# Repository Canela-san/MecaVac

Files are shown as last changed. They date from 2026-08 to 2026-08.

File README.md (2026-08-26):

# MecaVac

*Refrigerador inteligente para vacinas — controle de temperatura, monitoramento de porta e log de eventos em ESP32.*

**Mecatron Projetos e Consultoria Jr.** · Hardware (Altium Designer) + Firmware (ESP32 / PlatformIO) · 2022 · Projeto concluído e aprovado pelo cliente; descontinuado após a primeira versão.

Este repositório reúne o firmware, o projeto de hardware e a documentação técnica do MecaVac — internamente registrado na Mecatron como *Refrigerador de Vacinas* (projeto nº 0000034). Ele também guarda o histórico real de desenvolvimento: sketches de bancada, versões intermediárias do firmware e o início (incompleto) de uma segunda revisão, mantidos aqui como registro de como o projeto evoluiu, não como parte do build final.

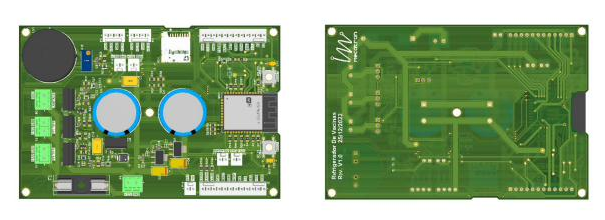
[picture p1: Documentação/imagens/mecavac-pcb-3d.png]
Renderização 3D da PCB do MecaVac — topo e fundo

gora
## Sumário

- [Sobre o projeto](#sobre-o-projeto)
- [Minha atuação](#minha-atuação)
- [Como funciona](#como-funciona)
- [Funcionalidades](#funcionalidades)
- [Hardware](#hardware)
- [Firmware](#firmware)
- [Estrutura do repositório](#estrutura-do-repositório)
- [Compilando e gravando o firmware](#compilando-e-gravando-o-firmware)
- [Lições aprendidas e limitações conhecidas](#lições-aprendidas-e-limitações-conhecidas)
- [Tecnologias utilizadas](#tecnologias-utilizadas)
- [Status do projeto](#status-do-projeto)
- [Licença e uso](#licença-e-uso)
- [Autor](#autor)

## Sobre o projeto

O MecaVac é um refrigerador para armazenamento de vacinas, desenvolvido sob demanda de um cliente que precisava de um equipamento com controle de temperatura confiável e rastreabilidade do que acontece dentro dele: quando a porta é aberta, quando uma vacina é retirada, e o que acontece em caso de queda de energia.

O equipamento final integra:

- placa de circuito impresso customizada, com ESP32 como controlador central;
- acionamento de dois módulos Peltier (TEC) para refrigeração, controlados por PWM;
- sensoriamento de porta, temperatura, retirada de vacina e falha dos módulos Peltier;
- display LCD local para status e configuração de data/hora;
- log de eventos em cartão microSD, com backup de energia via supercapacitores;
- provisionamento de Wi-Fi via portal cativo, para envio de status e logs a um servidor do cliente.

O projeto passou por testes de bancada e de campo, foi validado e aprovado pelo cliente. Depois da entrega, ficou claro que a primeira versão tinha vários pontos a melhorar (ver [Lições aprendidas](#lições-aprendidas-e-limitações-conhecidas)) — mas o custo de uma segunda revisão de hardware não se pagou para o cliente, e o projeto foi encerrado nessa primeira versão.

## Minha atuação

Entrei na Mecatron Jr. ainda no primeiro ano da faculdade, como Assessor de Projetos, e o MecaVac acabou ficando comigo do início ao fim: concepção, hardware, firmware, documentação e as reuniões — tanto internas quanto com o cliente que pagou pelo desenvolvimento. Como em qualquer empresa júnior brasileira, a atuação foi voluntária (empresas juniores não podem remunerar seus membros), mas foi a experiência mais próxima de um projeto real que tive até então: cliente pagante, prazo e responsabilidade técnica de ponta a ponta.

Principais responsabilidades:

- projeto completo da PCB no Altium Designer — esquemático, seleção de componentes, roteamento e liberação para fabricação;
- desenvolvimento do firmware em C/C++ (ESP32, PlatformIO);
- definição da arquitetura de log local (SD) e de comunicação com o servidor do cliente;
- documentação técnica do hardware e do firmware;
- interlocução direta com o cliente e com a diretoria da empresa júnior.

Aprovação técnica do projeto (Mecatron Jr.): Nisio José S. Neto.

## Como funciona

Em operação normal, o ESP32 lê periodicamente os três sensores de temperatura (DS18B20, barramento OneWire) e calcula a média entre as duas sondas do compartimento de vacinas. Essa média é comparada a uma temperatura ideal (6 °C) e o firmware ajusta a potência aplicada aos dois módulos Peltier em quatro patamares (0%, ~27%, ~50% e 100% de duty cycle), de acordo com o quanto a leitura está fora da faixa aceitável.

Um sensor magnético detecta a abertura da porta: ao abrir, a luz interna acende e o LED de status muda de verde para vermelho; se a porta ficar aberta além de um tempo configurável (10 segundos na versão final), o buzzer soa até que a porta seja fechada ou um dos botões externos seja pressionado. Cada módulo Peltier tem um sensor próprio de funcionamento, permitindo detectar falha em um dos dois de forma independente.

Um relógio de tempo real (DS1307) mantém data e hora mesmo sem conexão, usadas tanto na exibição do display quanto na marcação dos eventos gravados no cartão microSD. Se a alimentação principal cai, um sensor de queda de energia dispara e o firmware grava esse evento no SD — o equipamento continua ligado por alguns segundos graças a dois supercapacitores de 1F carregados por um circuito de soft-start, tempo suficiente para o log ser gravado com segurança antes do desligamento total.

Na primeira inicialização (ou após um reset de configurações), o dispositivo sobe uma rede Wi-Fi temporária para que alguém conecte um celular ou notebook e configure a rede definitiva com internet; a partir daí, o equipamento reporta status e histórico de eventos ao servidor do cliente. Enquanto não há conexão configurada, ou se ela cai, os logs continuam sendo salvos localmente no SD.

O display LCD 20x4 alterna entre diferentes telas de status (inicializando, temperatura + hora, porta aberta, conectado/não conectado à internet) e tem um modo de configuração de data/hora, acessado segurando os dois botões físicos por alguns segundos.

## Funcionalidades

- Controle de temperatura por PWM em dois módulos Peltier, com lógica por patamares a partir da média de dois sensores DS18B20 (terceiro sensor mantido como referência independente).
- Sensor dedicado de funcionamento em cada módulo Peltier, para detecção de falha.
- Monitoramento de porta (sensor magnético) com acionamento automático de luz interna e alarme sonoro após tempo configurável.
- Indicação visual de status via LED RGB.
- Display LCD 20x4 (I2C) com múltiplas telas de status e modo de configuração de data/hora.
- RTC (DS1307) para marcação temporal dos eventos.
- Log de eventos (porta, temperatura, quedas de energia) em cartão microSD, como redundância local independente da internet.
- Detecção de queda de energia com backup local (dois supercapacitores de 1F + circuito de soft-start), garantindo tempo para gravar o evento antes do desligamento.
- Provisionamento de rede Wi-Fi via portal cativo (sem credenciais fixas no firmware), com envio de status e logs a um servidor remoto do cliente.
- Leitura de retirada de vacinas por meio de uma rede de microswitches decodificada em uma única entrada analógica (ver detalhe em [Lições aprendidas](#lições-aprendidas-e-limitações-conhecidas)).

## Hardware

A PCB foi projetada por mim no Altium Designer — meu primeiro projeto de placa desse porte, com processador, múltiplos subsistemas de sensoriamento, drivers de potência e gerenciamento de energia integrados em uma placa só.

### Especificações da PCB

| Item | Especificação |
|---|---|
| Controlador | ESP32-WROOM-32D |
| Camadas | 2 (top/bottom), cobre 0,30 mm por camada |
| Substrato | FR-4, dielétrico 0,96 mm |
| Espessura total | 1,60 mm |
| Dimensões (placa) | ~76 × 71 mm |
| Encaixe mecânico | ~120 × 80 mm |
| Furos | 143 (50 vias de 0,30 mm + furos de montagem/componentes em diversos diâmetros) |
| Alimentação | Entrada 12 V, com reguladores lineares para 5 V e 3,3 V |
| Proteção de entrada | Diodo TVS 15 V |
| Backup de energia | 2× supercapacitor 1F / 5,5 V com circuito de soft-start |

### Destaques de projeto

- **Recorte sob a antena do ESP32-WROOM-32D**: a área de cobre logo abaixo da antena integrada do módulo foi removida do plano de referência, seguindo a recomendação do fabricante, para reduzir a interferência no sinal Wi-Fi.
- **Drivers de potência** para os dois módulos Peltier e para a lâmpada interna, com MOSFETs de canal N (IRF1404PBF) acionados por um par de transistores BC846/BC807 fazendo o drive de gate.
- **Backup de energia** com dois supercapacitores de 1F / 5,5 V e circuito de soft-start (limitação de inrush no carregamento), dedicado a manter o sistema vivo por alguns segundos após uma queda de energia — tempo suficiente para gravar o evento no cartão SD.
- **Leitura de retirada de vacina por escada resistiva**: em vez de uma entrada digital por compartimento, o hardware usa uma rede de microswitches com resistores em escada, lida por uma única entrada analógica — cada combinação de chaves fechadas gera um nível de tensão distinto, decodificado em firmware para identificar qual compartimento (até 15) teve uma vacina retirada.

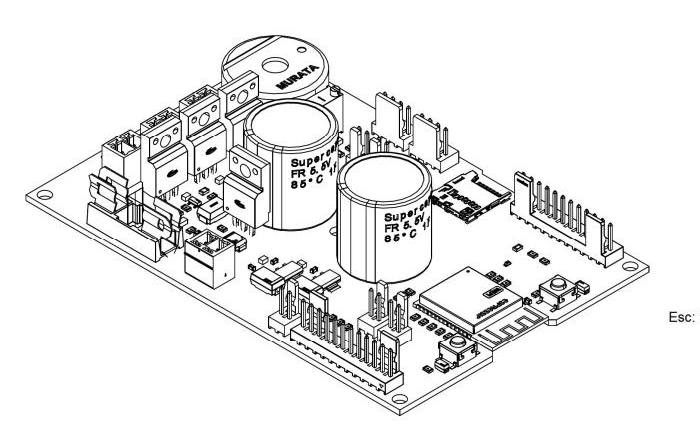
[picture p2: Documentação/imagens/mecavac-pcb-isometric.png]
Vista trica da PCB (Altium 3D)


### Principais componentes

| Componente | Função |
|---|---|
| ESP32-WROOM-32D | Microcontrolador principal |
| LM1117IMP-3.3 / LM1117MPX-5.0 | Reguladores lineares 3,3 V e 5 V |
| IRF1404PBF (×4) | MOSFETs de potência — Peltier 1, Peltier 2, lâmpada e soft-start |
| BC846BLT1G / BC807-40-7-F | Transistores de drive de gate |
| Supercapacitor 1F / 5,5 V (×2) | Backup de energia |
| DS1307 | RTC (relógio de tempo real, módulo externo à PCB) |
| DS18B20 (×3) | Sensores de temperatura (OneWire) |
| PKB24SPCH3601-B0 | Buzzer piezoelétrico (alarme) |
| TVS-15V | Proteção contra transientes na entrada de 12 V |

A lista completa de materiais (BOM) e as folhas de fabricação (camadas, drill table, indicação de conectores) estão na documentação técnica exportada em `Documentação/`.

### Mapeamento de pinos (ESP32)

| Pino | Função | Referência na PCB |
|---|---|---|
| EN | Reset da CPU | RST |
| IO00 | Habilita gravação de firmware | BOOT |
| IO02 | Cartão microSD — CS/SS | – |
| IO04 | Controle PWM dos módulos Peltier | – |
| IO05 | LED RGB — canal azul | LED B |
| IO12 | Sensor de funcionamento — Peltier 1 | – |
| IO13 | Sensor de funcionamento — Peltier 2 | – |
| IO14 | Sensor magnético — porta 1 | MAG1 |
| IO15 | Sensor magnético — porta 2 | MAG2 |
| IO16 | LED RGB — canal vermelho | LED R |
| IO17 | LED RGB — canal verde | LED G |
| IO18 | Cartão microSD — CLK | – |
| IO19 | Cartão microSD — MISO | – |
| IO21 | I2C — SDA (display / RTC) | SDA |
| IO22 | I2C — SCL (display / RTC) | SCL |
| IO23 | Cartão microSD — MOSI | – |
| IO25 | Lâmpada interna (12 V) | LAMP |
| IO26 | Barramento OneWire — 3× DS18B20 | TERM |
| IO27 | Botão externo 1 (navegação display) | B1 |
| IO32 | Botão externo 2 (navegação display) | B2 |
| IO33 | Buzzer (alarme sonoro) | – |
| IO34 | Rede de microswitches — retirada de vacina | RET |
| IO35 | Sensor de queda de energia | – |

### Conectores externos

| Conector / lado | Sinais |
|---|---|
| Botões do monitor 1 e 2 | +3,3 V, B1 / B2 |
| Display LCD | +5 V, SCL, SDA, GND |
| RTC (módulo externo) | +3,3 V, SCL, SDA, GND |
| Sensor magnético — porta 1 e 2 | +3,3 V, MAG1 / MAG2 |
| Sensores de temperatura (3×, em paralelo) | +3,3 V, TERM, GND |
| Sensor de retirada de vacina | +3,3 V, VAC, GND |
| Peltier 1 / Peltier 2 | +12 V, GND |
| Lâmpada interna | +12 V, GND |
| LED RGB | LED R, LED G, LED B, GND |
| Coolers 1, 2 e 3 (dissipação térmica) | +12 V, GND |
| Entrada de energia | +12 V, GND |

O pinout completo dos conectores (P1–P11, J1, J2) está na documentação técnica exportada em `documentação/`.

## Firmware

O firmware roda sobre o **framework Arduino para ESP32**, gerenciado via **PlatformIO** (`Firmware/platformio.ini`, ambiente `esp32dev`).

### Bibliotecas utilizadas

- `Wire` — comunicação I2C (display e RTC)
- `LiquidCrystal_I2C` — display LCD 20x4
- `OneWire` + `DallasTemperature` — sensores de temperatura DS18B20
- `SD`, `SPI`, `FS` — cartão microSD
- `WiFi`, `DNSServer`, `ESPAsyncWebServer`, `ESPAsyncWiFiManager` — provisionamento de rede e portal cativo
- API nativa do ESP32 (`ledcSetup` / `ledcAttachPin` / `ledcWrite`) — PWM dos módulos Peltier

### Arquitetura

O `loop()` principal é organizado em blocos sequenciais e não bloqueantes (baseados em `millis()`, sem `delay()` na lógica crítica): leitura e debounce de portas e botões, controle de luz e alarme, leitura da rede de microswitches de retirada de vacina, controle de temperatura/PWM dos Peltiers, monitoramento de queda de energia, leitura do RTC, máquina de estados do display (telas de status + modo de configuração) e o provisionamento de Wi-Fi.

A comunicação com o servidor do cliente foi desenhada em torno de códigos de evento (por exemplo: boot, abertura/fechamento de porta, retirada de vacina, queda de energia) — visíveis nos comentários `// SERVIDOR: ...` espalhados pelo código, que documentam o protocolo pensado para o envio de dados.

### Histórico de desenvolvimento (`Firmware/src/`)

O firmware evoluiu por meio de sketches de bancada, testando cada subsistema isoladamente antes da integração final. Esses arquivos foram mantidos no repositório como histórico real do desenvolvimento — não como parte do build final.

| Arquivo | O que é |
|---|---|
| `main.cpp` | **Firmware final**, integrado e entregue ao cliente. |
| `testes.cpp` | Evolução mais avançada do firmware principal: adiciona suporte experimental a uma segunda porta e um log mais estruturado no SD. Ficou incompleto (há erros de sintaxe) quando o projeto foi descontinuado. |
| `test_arduino.cpp` | Snapshot intermediário do firmware principal, ainda com a pinagem de uma revisão anterior da placa. |
| `teste_buzzer.cpp` | Bring-up consolidado de porta, luz interna, LED RGB e buzzer, anterior à integração de display e RTC. |
| `paginação_dispcomp.cpp` | Rascunho inicial da máquina de estados do display — mais ambicioso que a versão final (previa seleção de idioma, unidade °C/°F, beep de navegação e lembrete de troca de filtro, cortados do escopo final). |
| `base_display.cpp` | Teste de inicialização do LCD 20x4 via I2C. |
| `teste_RTC.cpp` | Teste de leitura/escrita do RTC DS1307. |
| `endereços_sens_temp.cpp` | Varredura do barramento OneWire para descobrir os endereços únicos de cada DS18B20. |
| `leit_sens_temp.cpp` | Teste de leitura simultânea das 3 sondas de temperatura. |
| `teste_peltier.cpp` | Bancada de calibração do driver de Peltier (ajuste manual de duty cycle via serial, com leitura em display OLED). |
| `teste_peltier2.cpp` | Teste simples de PWM (fade) no canal do MOSFET do Peltier. |
| `config_saidavac.cpp` | Calibração experimental dos limiares de tensão da rede de microswitches de retirada de vacina. |
| `aperto_botão.cpp` | Estudo de debounce de botão. |
| `base_SD.cpp` | Utilitários de cartão SD (listar, ler, escrever, renomear, apagar). |
| `conect_wifi.cpp` | Teste isolado do provisionamento Wi-Fi via portal cativo (AsyncWiFiManager). |
| `serv_web.cpp` | Protótipo de referência (baseado em tutorial externo, ver comentário no arquivo) para servidor web embarcado — não integrado à versão final. |

> Como cada um desses arquivos tem sua própria função `setup()`/`loop()`, eles **não compilam juntos**. Para montar apenas o firmware final, veja [Compilando e gravando o firmware](#compilando-e-gravando-o-firmware).

## Estrutura do repositório

```
MecaVac/
├── Firmware/                     # Projeto PlatformIO (ESP32, framework Arduino)
│   ├── src/
│   │   ├── main.cpp                # Firmware final
│   │   └── ...                     # Sketches de bring-up (ver tabela acima)
│   ├── lib/
│   ├── include/
│   ├── test/
│   └── platformio.ini
├── Hardware/                     # Projeto Altium Designer
│   ├── MecaVac.PrjPcb
│   ├── MecaVac.SchDoc
│   ├── MecaVac.PcbDoc
│   └── v2 (descontinuada)/         # Início não finalizado de uma segunda revisão
├── Documentação/
│   ├── imagens/                     # Imagens usadas neste README
│   └── Documentação_Refrigerador_de_Vacinas.pdf   # Exportação técnica (dimensões, BOM, pinout, camadas)
└── README.md
```

> A pasta `Hardware/` é mantida principalmente como backup do projeto Altium. Ajuste os nomes e caminhos acima conforme a organização real da sua cópia local — alguns arquivos da segunda revisão (nunca finalizada) podem estar incompletos ou ausentes.

## Compilando e gravando o firmware

Pré-requisitos: [PlatformIO](https://platformio.org/) (CLI ou extensão do VSCode) e uma placa ESP32 DevKit.

1. Clone o repositório.
2. Dentro de `Firmware/src/`, mantenha apenas `main.cpp` (mova os demais arquivos de teste para fora da pasta `src/`, já que todos possuem `setup()`/`loop()` próprios e são compilados juntos por padrão pelo PlatformIO).
3. Confirme os endereços dos sensores DS18B20 (`Probe01`, `Probe02`, `Probe03`) em `main.cpp` — use `endereços_sens_temp.cpp` para descobrir os endereços do seu hardware, caso sejam diferentes.
4. Compile e grave:

   ```bash
   cd Firmware
   pio run --target upload
   ```

5. Acompanhe os logs pela serial:

   ```bash
   pio device monitor -b 115200
   ```

## Lições aprendidas e limitações conhecidas

Esta foi minha primeira PCB de porte relevante, e a experiência deixou aprendizados concretos — alguns só ficaram claros depois dos testes de campo:

- **Driver de potência superdimensionado.** Um professor de eletrônica avaliou o driver dos Peltiers/lâmpada (MOSFET + par de transistores BC846/BC807 para acionamento de gate) e apontou que o mesmo resultado seria possível com bem menos componentes. Foi um dos principais pontos mapeados para revisão em uma eventual segunda versão.
- **Conflito de pino entre a leitura de retirada de vacina e o PWM do Peltier.** Na integração final, o pino usado para decodificar a rede de microswitches de retirada de vacina (`leitura`, GPIO4) ficou mapeado para o mesmo pino da saída PWM dos módulos Peltier (`peltier`, GPIO4) — por isso essa leitura ficou comentada em `main.cpp`, funcionando apenas nos sketches de bancada (`config_saidavac.cpp` e versões anteriores do firmware).
- **Comunicação com o servidor documentada, mas não totalmente implementada no firmware.** O protocolo de códigos de evento para o servidor do cliente foi definido (comentários `// SERVIDOR: ...` no código), mas parte do envio ainda estava em desenvolvimento quando o projeto foi encerrado.
- **Segunda versão não viabilizada.** Os pontos acima, entre outros menores, motivaram o início de uma segunda revisão de hardware — mas o custo adicional não se justificou para o cliente depois da primeira entrega, e o projeto foi formalmente encerrado na v1, mesmo aprovado e funcional.

## Tecnologias utilizadas

`Altium Designer` · `ESP32` · `C/C++ (Arduino Framework)` · `PlatformIO` · `I2C` · `OneWire` · `SPI` · `Wi-Fi (WiFiManager / ESPAsyncWebServer)` · `RTC DS1307` · `DS18B20` · `Gerenciamento de energia (supercapacitores)` · `Git`

## Status do projeto

Concluído, testado e **aprovado pelo cliente** em 2022. Descontinuado logo após a entrega, sem uma segunda versão programada. Este repositório é mantido como referência técnica e de portfólio pessoal.

## Licença e uso

Este projeto foi desenvolvido sob demanda para um cliente da Mecatron Projetos e Consultoria Jr., que é o proprietário do produto final. O conteúdo deste repositório é disponibilizado publicamente como portfólio técnico pessoal e registro de desenvolvimento, não sob uma licença de código aberto.

## Autor

**Gabriel Canela** — desenvolvido durante a atuação como Assessor de Projetos na Mecatron Projetos e Consultoria Jr.

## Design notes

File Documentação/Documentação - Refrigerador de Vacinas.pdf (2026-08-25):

# D3 TVS⁻¹⁵V

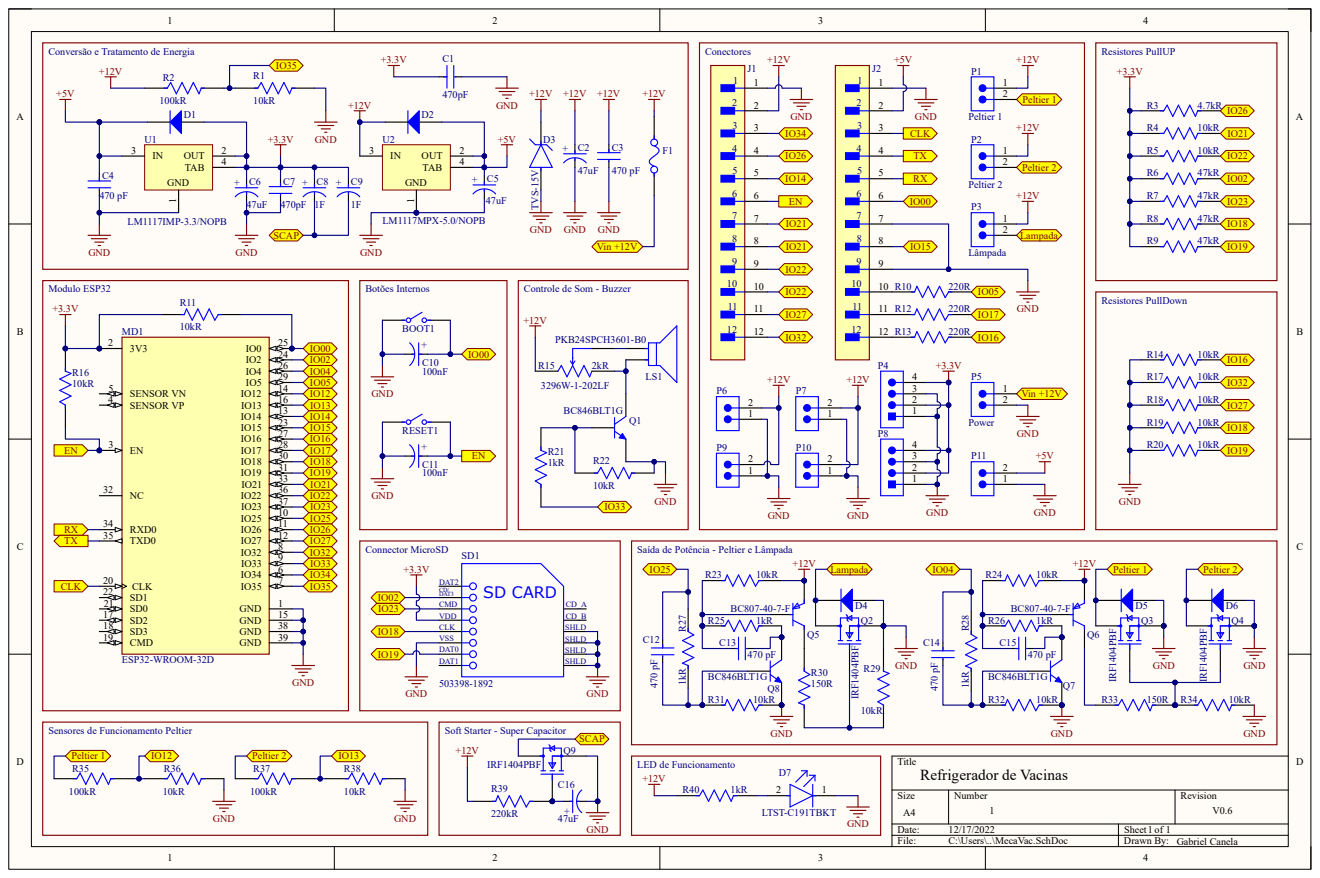
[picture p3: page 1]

Conversão e Tratamento de Energia

Controle de Som - Buzzer

Saída de Potência - Peltier e Lâmpada

Sensores de Funcionamento Peltier

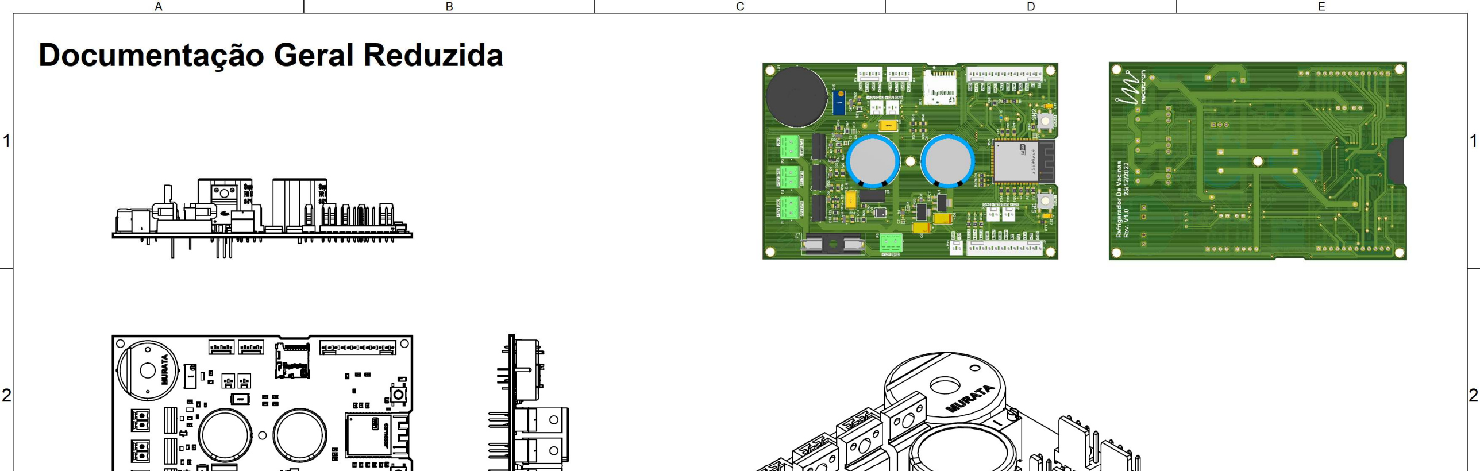
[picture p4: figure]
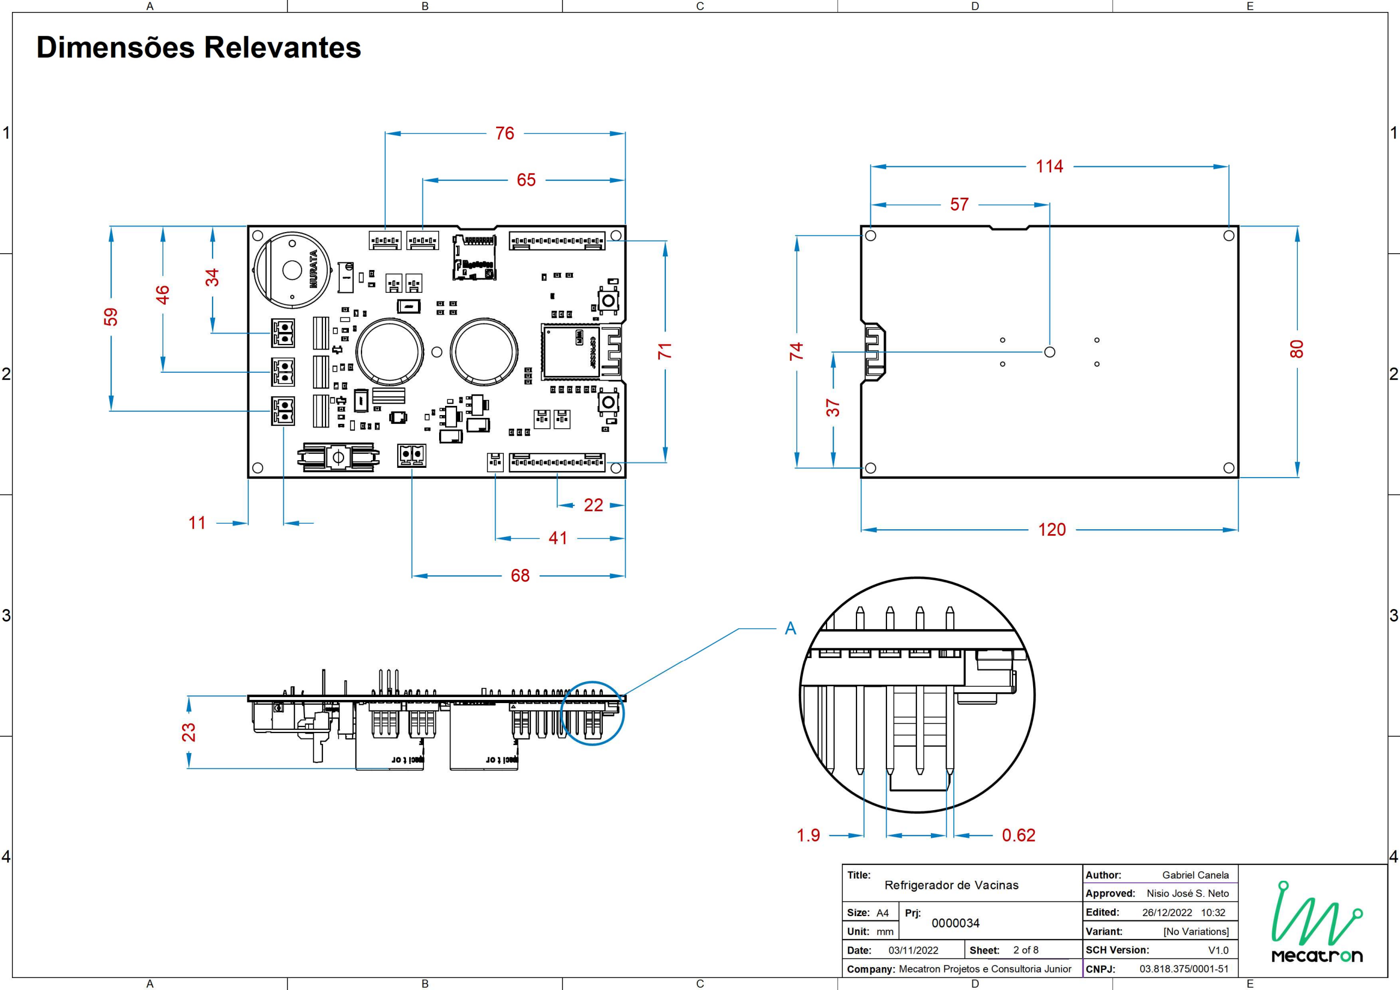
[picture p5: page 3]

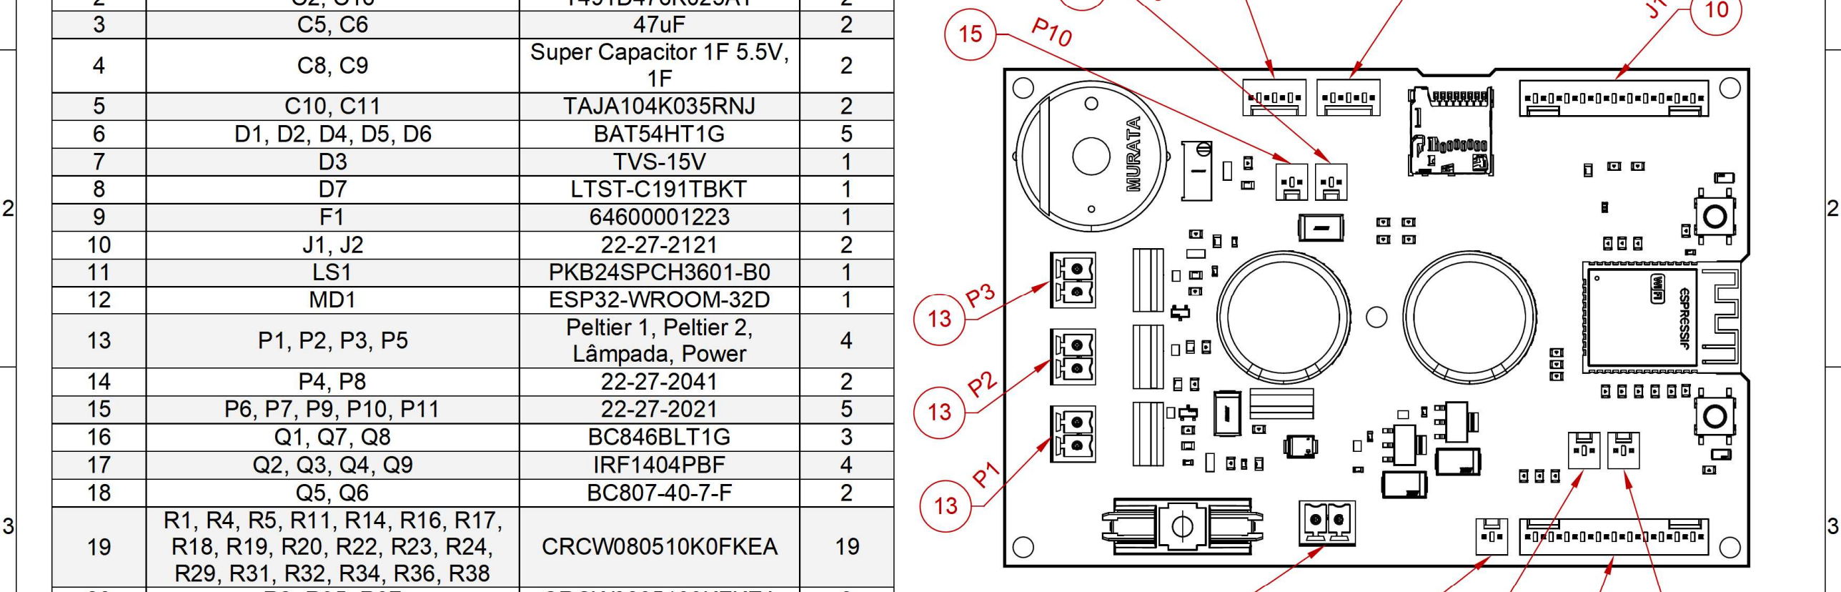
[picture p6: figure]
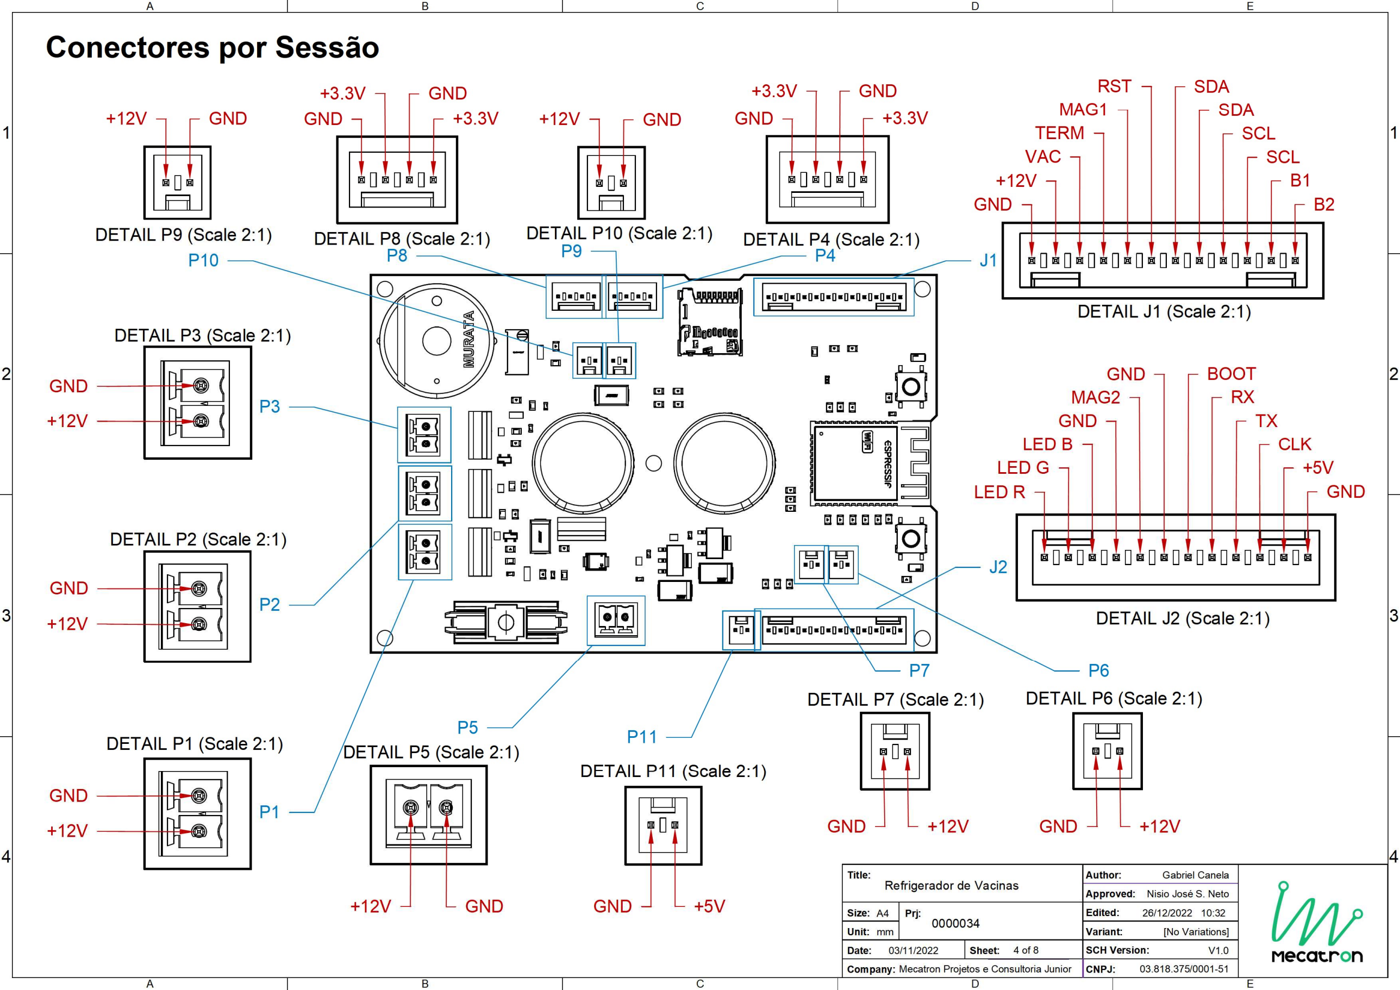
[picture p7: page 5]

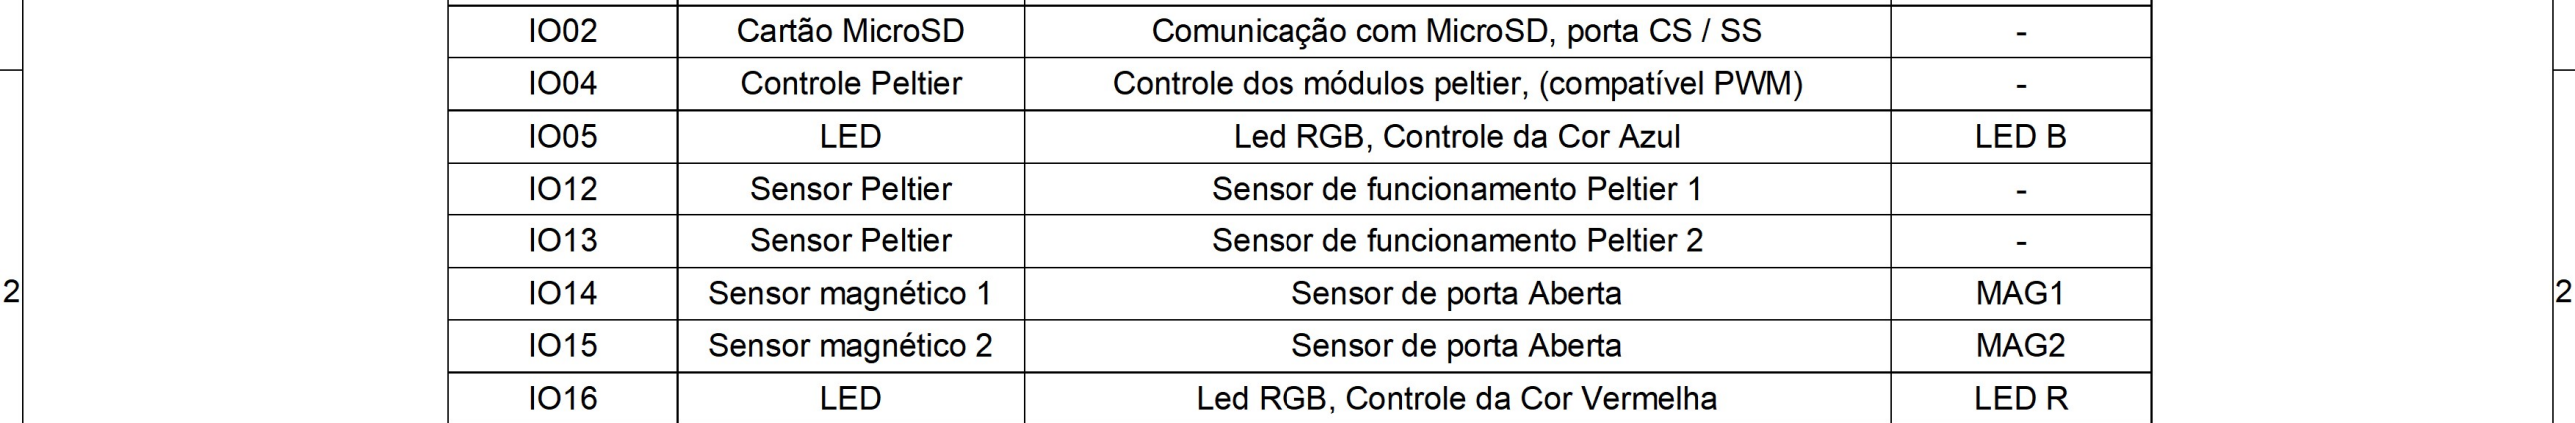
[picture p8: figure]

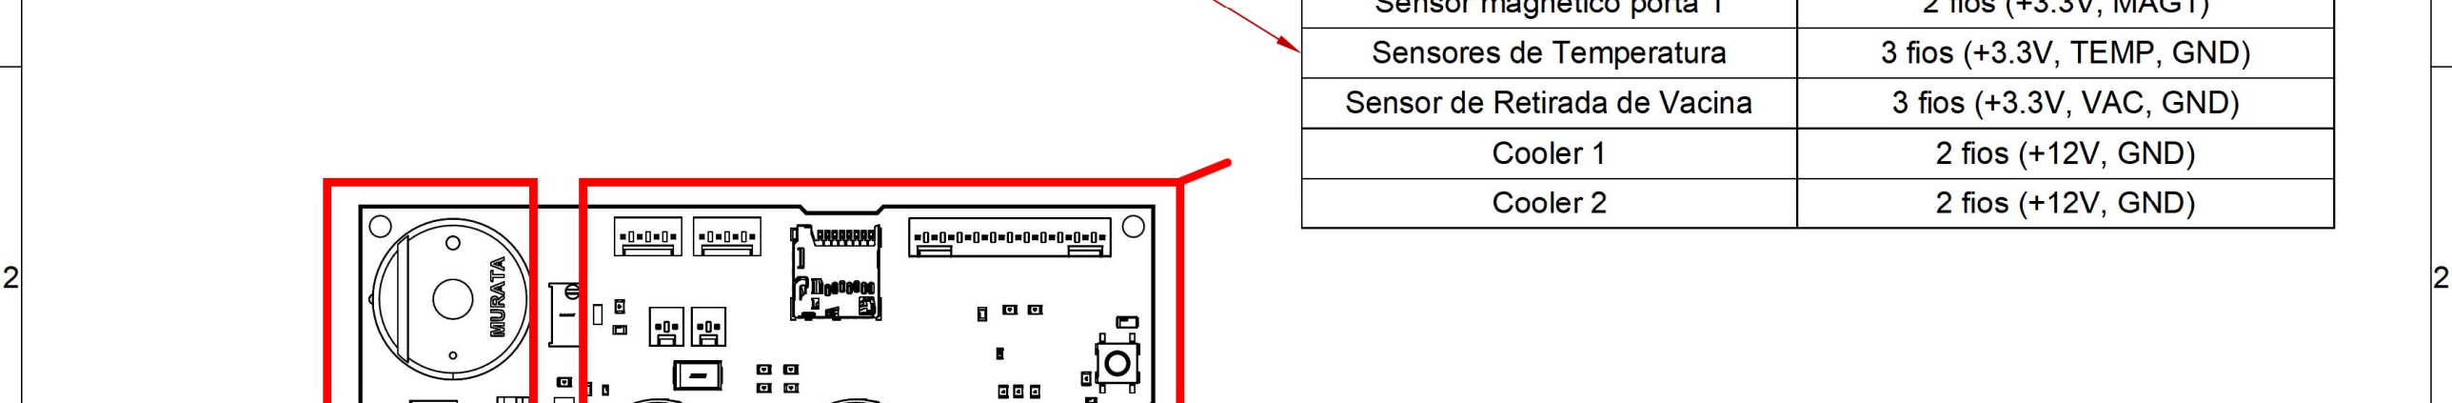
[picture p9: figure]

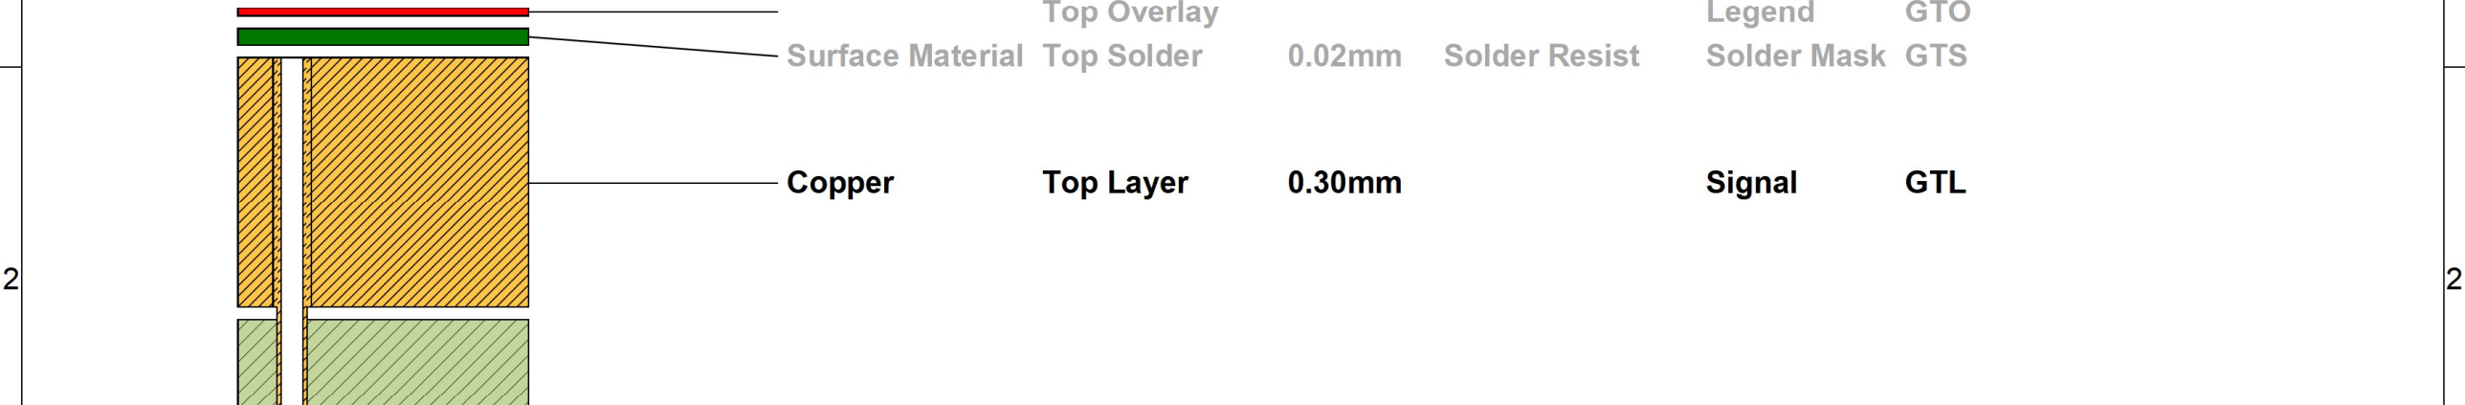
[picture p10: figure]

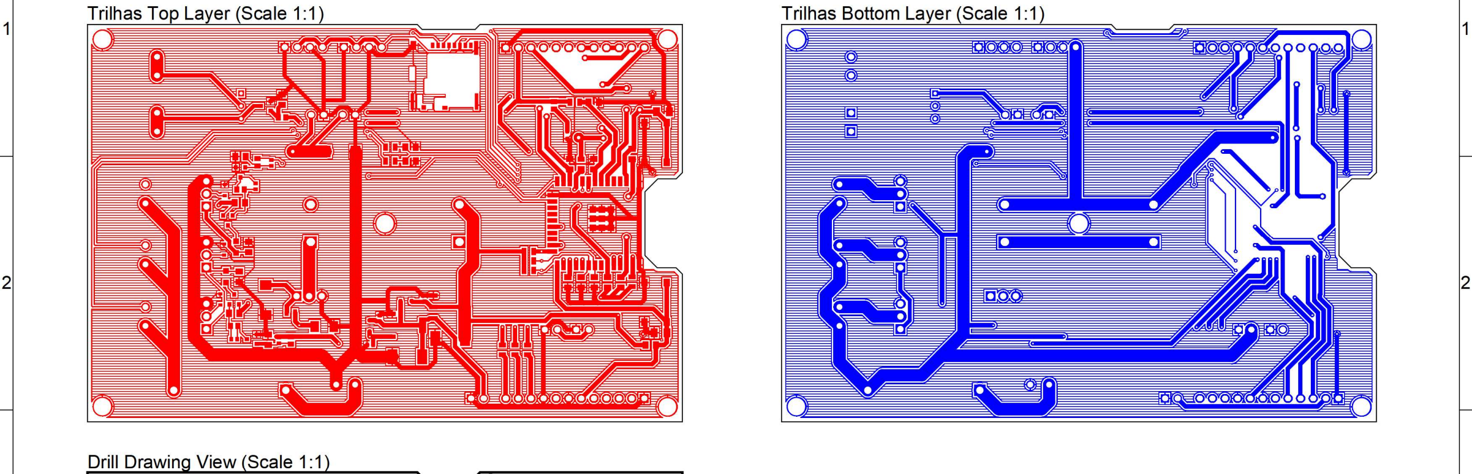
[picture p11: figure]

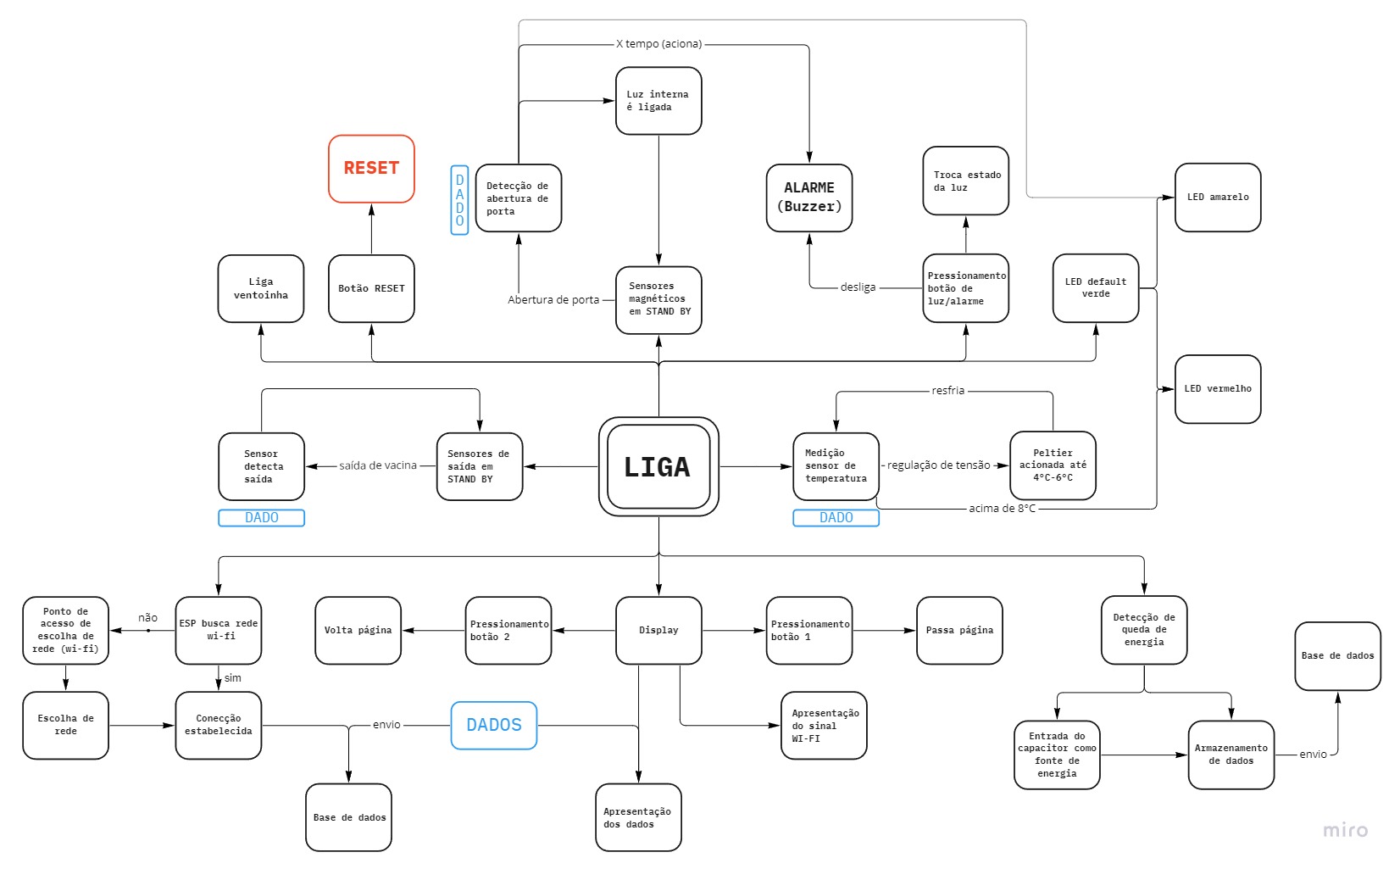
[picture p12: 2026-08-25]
Documentação/imagens/Máquina de estados MecaVac.jpg

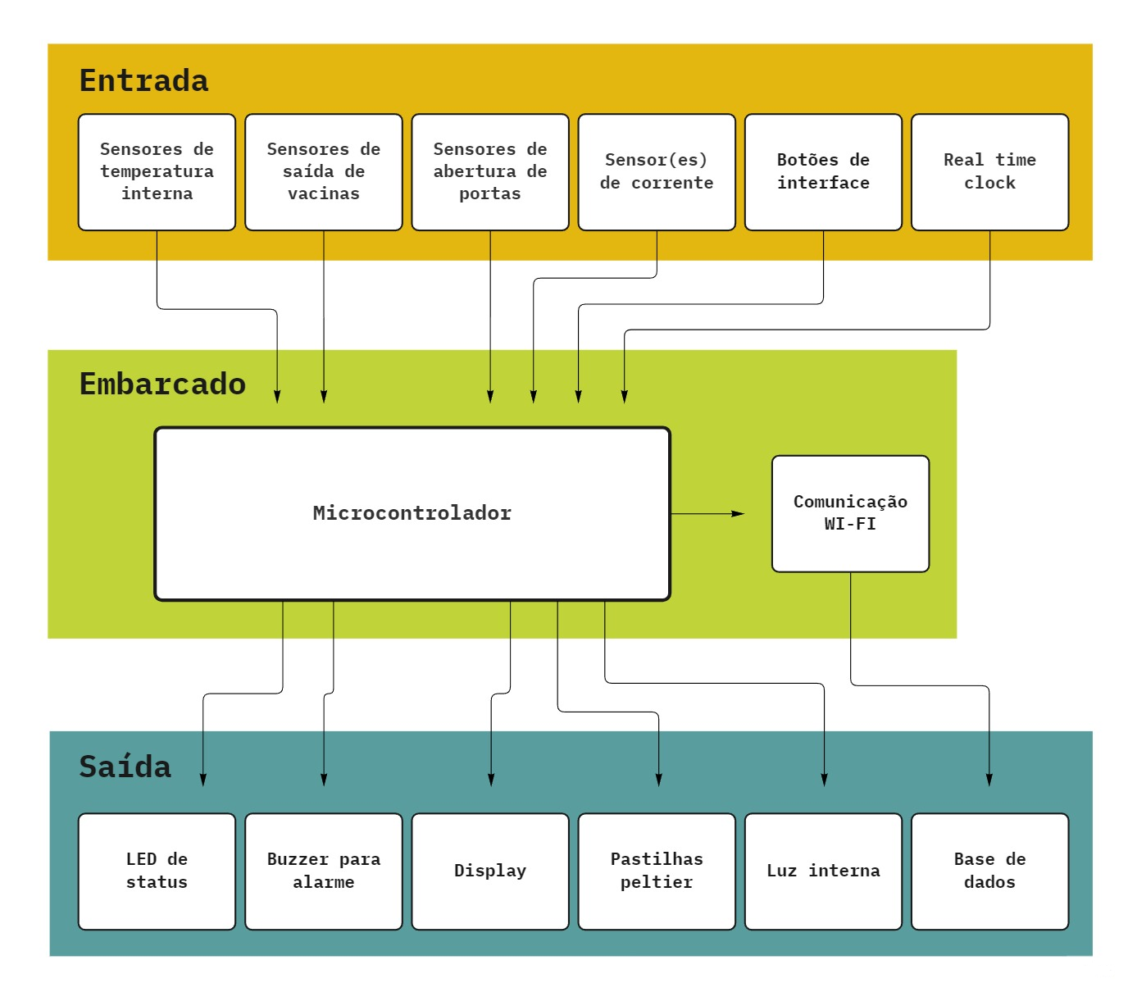
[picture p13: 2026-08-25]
Documentação/imagens/Arquitetura do sistema.png

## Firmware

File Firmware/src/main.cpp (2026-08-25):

String versao = "V1.0.0";
bool reset = false;
bool flag_liga = true;

// Variáveis servidor ||||||||||||||||||||||||||||||||||||||||||||||||||||||||||||||||||||||||||||||||||||||||||||||||||||||||||||||

#include <DNSServer.h> 
#include <ESPAsyncWebServer.h>
#include <ESPAsyncWiFiManager.h>   
#include <WiFi.h>

AsyncWebServer server(80); //Cria os objetos dos servidores
DNSServer dns;
unsigned long temp_wifi = 0;
int wifi_flag = 1;

int conectado = 0;
// Cartão SD |||||||||||||||||||||||||||||||||||||||||||||||||||||||||||||||||||||||||||||||||||||||||||||||||||||||||||||||||||||||

#include "FS.h"
#include "SD.h"
#include "SPI.h"

// Variáveis botões + portas |||||||||||||||||||||||||||||||||||||||||||||||||||||||||||||||||||||||||||||||||||||||||||||||||||||||

int luz_interna = 25;
int RGBverde = 17;
int RGBvermelho = 16;
int sens_porta1 = 14;
int est_ini_por1 = 0;
int est_ini_por2 = 0;
int est_ini_por4 = 0;
int est_ini_bot = 0;
int prim_press = 1;
int prim_press2 = 1;
int prim_press3 = 1;
int prim_press4 = 1;
int estado_botao = LOW;
int estado_luz = LOW;
int alarme_tocando = LOW;
int alarme = 33;
int estado_verde = HIGH;
int estado_vermelho = LOW;
long tempo_ult_debouce1 = 10; //mudar para ajustar
long tempo_ult_debouce2 = 10; //mudar para ajustar
long tempo_ult_debouce3 = 10; //mudar para ajustar
long tempo_ult_debouce4 = 10; //mudar para ajustar
long delay_debouce1 = 0;
long delay_debouce2 = 0;
long delay_debouce3 = 0;
long delay_debouce4 = 0;
long delay_alarme = 10000;
unsigned long tempo_alarme = 0; 
unsigned long tempo_atual = 0;

// Variáveis RTC||||||||||||||||||||||||||||||||||||||||||||||||||||||||||||||||||||||||||||||||||||||||||||||||||||||||||||||||||||

#define DS1307_ADDRESS 0x68
byte zero = 0x00;
unsigned long temp_set = 0;

// Variáveis controle de temepratura |||||||||||||||||||||||||||||||||||||||||||||||||||||||||||||||||||||||||||||||||||||||||||||||

#include <OneWire.h>
#include <DallasTemperature.h>
unsigned long tempo_anteriorT = 0;
const unsigned long tempo_temp = 30000;
float ideal = 6.0;


#define ONE_WIRE_BUS_PIN 26  // declarar o pino de entrada dos sensores

// Setup a oneWire instance to communicate with any OneWire devices
OneWire oneWire(ONE_WIRE_BUS_PIN);

// Pass our oneWire reference to Dallas Temperature.
DallasTemperature sensors(&oneWire);
float temp1 = 0.0;
float temp2 = 0.0;
float temp3 = 0.0;
float temp3F = 0.0;
float media_tempC = 0.0;
float media_tempF = 0.0;
bool uni_Celc = true;


// Assign the addresses of your 1-Wire temp sensors
DeviceAddress Probe01 = { 0x28, 0x74, 0x22, 0x96, 0xF0, 0x1, 0x3C, 0x9D };
DeviceAddress Probe02 = { 0x28, 0xE4, 0x4A, 0x96, 0xF0, 0x1, 0x3C, 0x3 };
DeviceAddress Probe03 = { 0x28, 0xE8, 0x9C, 0x96, 0xF0, 0x1, 0x3C, 0xBC };

// Variáveis peltier |||||||||||||||||||||||||||||||||||||||||||||||||||||||||||||||||||||||||||||||||||||||||||||||||||||||||||||||

#include <Wire.h>

int peltier = 4;  // The N-Channel MOSFET is on digital pin 3
int canal = 0;
int resolucao = 8;
int freq = 5000;                                 
int peltier_level = 0;  // This is a value from 0 to 255 that actually controls the MOSFET

// Variáveis saída de vacinas |||||||||||||||||||||||||||||||||||||||||||||||||||||||||||||||||||||||||||||||||||||||||||||||||||||||||

int sinal_vac = 357;  // editar GPiO
int saida_vac = 0;
int leitura = 4;
bool prim_acion = true;

// Variáveis display ||||||||||||||||||||||||||||||||||||||||||||||||||||||||||||||||||||||||||||||||||||||||||||||||||||||||||||||||||

#include <LiquidCrystal_I2C.h>
LiquidCrystal_I2C lcd(0x3F,20,4);   //endereço "adaptador" i2C

bool estado_1 = false;
bool estado_234 = false;
bool estado_69 = false;
bool estado_69A = false;
bool estado_79 = false;
bool estado_79A = false;
bool estado_8 = false;
bool estado_year = false;
bool estado_month = false;
bool estado_day = false;
bool estado_hour = false;
bool estado_min = false;
bool estado_saved = false;
bool config = false;
bool trava_millis = false;
bool config1 = true;
bool config2 = true;
bool prim8 = true;

unsigned long temp_presave = 0;
unsigned long temp_saved = 0;
unsigned long temp_iniPress = 0;
unsigned long temp_iniPress2 = 0;
unsigned long temp_iniRefresh = 0;
unsigned long temp_refresh = 200;
unsigned long temp_config = 0;
unsigned long temp_reset = 0;
unsigned long temp_pag = 0;
unsigned long temp_debugp = 0;
unsigned long blinkTime = 0;
String placeHolder = "  ";

int ultima = 0;
int flag_presave = 1;
int release = 0;
int prim_config = 1;
int prim_sim = LOW;
int prim_sim2 = LOW;
int bot_dir = 32;
int bot_esq = 27;
int est_ini_botD = 0;
int est_ini_botE = 0;
int prim_pressD = 1;
int prim_pressE = 1;
int tempo_ult_debouceD = 10;
int tempo_ult_debouceE = 10;
int delay_debouceD = 0;
int delay_debouceE = 0;
int estado_botaoD = LOW;
int estado_botaoE = LOW;
unsigned long tempo_inicializacao = 0;

// Controle queda de energia ||||||||||||||||||||||||||||||||||||||||||||||||||||||||||||||||||||||||||||||||||||||||||||||||||||||

int entrada_energ = 35;
int leitura_energ = 0;
bool prim_leit = true;
unsigned long tempo_anteriorE = 0;
const unsigned long tempo_energ = 100;

// Falha peltier |||||||||||||||||||||||||||||||||||||||||||||||||||||||||||||||||||||||||||||||||||||||||||||||||||||||||||||||||

int sens_energ1 = 12;
int sens_energ2 = 13;

//||||||||||||||||||||||||||||||||||||||||||||||||||||||||||||||||||||||||||||||||||||||||||||||||||||||||||||||||||||||||||||||||

void setup() {

  //SERVIDOR: Código 10 (Boot normal)
  //SERVIDOR: Código 70, dado 40 (Liga -> ler se ter arquivo no SD -> Queda de energia servidor)

  pinMode(leitura, INPUT);
  pinMode(sens_porta1, INPUT);
  //pinMode(sens_porta2, INPUT);
  pinMode(luz_interna, OUTPUT);
  pinMode(alarme, OUTPUT);
  pinMode(peltier, OUTPUT);
  pinMode(RGBverde, OUTPUT);
  pinMode(RGBvermelho, OUTPUT);
  pinMode(entrada_energ, INPUT);
  pinMode(bot_dir, INPUT);
  pinMode(bot_esq, INPUT);
  pinMode(sens_energ1, INPUT);
  pinMode(sens_energ2, INPUT);
  Serial.begin(115200);

  Wire.begin();

  Wire.beginTransmission(DS1307_ADDRESS);
  Wire.write(zero);
  Wire.endTransmission();

  Wire.requestFrom(DS1307_ADDRESS, 7);

  int seg = bcdToDec(Wire.read());
  int min = bcdToDec(Wire.read());
  int hor = bcdToDec(Wire.read() & 0b111111);  // Formato 24 horas
  int diasem = bcdToDec(Wire.read());        // 0-6 -> Domingo - Sábado
  int di = bcdToDec(Wire.read());
  int me = bcdToDec(Wire.read());
  int an = bcdToDec(Wire.read());

  setDateTime(seg, min, hor, diasem, di, me, an);

  // initialize the Temperature measurement library
  sensors.begin();
  // set the resolution to 12 bit (Can be 9 to 12 bits .. lower is faster)
  sensors.setResolution(Probe01, 12);
  sensors.setResolution(Probe02, 12);
  sensors.setResolution(Probe03, 12);
  ledcSetup(canal, freq, resolucao);   // descomentar para ESP
  ledcAttachPin(peltier, canal);       // descomentar para ESP

  lcd.init();
  lcd.backlight();

  if(!SD.begin()){
    Serial.println("Card Mount Failed");
    return;
  }
  uint8_t cardType = SD.cardType();

  if(cardType == CARD_NONE){
    Serial.println("No SD card attached");
    return;
  }
}

//|||||||||||||||||||||||||||||||||||||||||||||||||||||||||||||||||||||||||||||||||||||||||||||||||||||||||||||||||||||||||||||||||

void loop() {
  Serial.println(conectado);
  tempo_atual = millis();

// Wifi |||||||||||||||||||||||||||||||||||||||||||||||||||||||||||||||||||||||||||||||||||||||||||||||||||||||||||||||||||||||||||

  if(wifi_flag == 1){
    wifi_flag = 0;
    AsyncWiFiManager manager(&server, &dns); //Cria o objeto do gerenciador
    manager.setTimeout(60); //timeout após 5 min (testar e chamar na hora certa)
    Serial.println(); // Imprime o endereço de IP que teremos que entrar no navegador
    manager.resetSettings(); //Reseta as configurações do gerenciador
    manager.autoConnect("Chiller"); //Cria o ponto de acesso com o nome RefriVac 
    Serial.println("Conectado"); //Imprime a mensagem de confirmação
    Serial.print("IP Address: ");
    Serial.println(WiFi.localIP());
  }

  temp_wifi = tempo_atual;
  if(millis() == temp_wifi + 1000){
    temp_wifi = 0;
    if (WiFi.status() == WL_CONNECTED){
      conectado = 1;
    }
    else{
      conectado = 0;
    }
  }
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

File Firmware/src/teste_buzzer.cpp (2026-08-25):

int luz_interna = 15;
int RGBverde = 26;
int RGBvermelho = 25;
int sens_porta1 = 14;
int est_ini_por1 = 0;
int est_ini_por2 = 0;
int est_ini_por4 = 0;
int est_ini_bot = 0;
int botao_AP = 32;
int prim_press = 1;
int prim_press2 = 1;
int prim_press3 = 1;
int prim_press4 = 1;
int estado_botao = LOW;
int estado_luz = LOW;
int alarme_tocando = LOW;
int alarme = 13;
int estado_verde = HIGH;
int estado_vermelho = LOW;
long tempo_ult_debouce1 = 10; //mudar para ajustar
long tempo_ult_debouce2 = 10; //mudar para ajustar
long tempo_ult_debouce3 = 10; //mudar para ajustar
long tempo_ult_debouce4 = 10; //mudar para ajustar
long delay_debouce1 = 0;
long delay_debouce2 = 0;
long delay_debouce3 = 0;
long delay_debouce4 = 0;
long delay_alarme = 3000;
unsigned long tempo_alarme = 0; 
unsigned long tempo_atual = 0;

void setup() {
  
    pinMode(sens_porta1, INPUT);
    pinMode(luz_interna, OUTPUT);
    pinMode(alarme, OUTPUT);
    pinMode(RGBverde, OUTPUT);
    pinMode(RGBvermelho, OUTPUT);
    pinMode(botao_AP, INPUT);
    Serial.begin(9600);
}

void loop() {
  
    tempo_atual = millis();
    if (analogRead(sens_porta1) < 4000 && est_ini_por1 == 0){  //detecção abertura porta 1
        if ((millis() - tempo_ult_debouce1) > delay_debouce1){
            est_ini_por1 = 1; // aberta
            tempo_ult_debouce1 = millis();
        }
    }
    else{
        if (est_ini_por1 == 1 && analogRead(sens_porta1) > 4000){
            est_ini_por1 = 0; // fechada
            prim_press2 = 1;
            prim_press4 = 1;
        }
    }

    if (analogRead(sens_porta1) > 4000 && est_ini_por4 == 0){  //detecção fechamento porta 1
        if ((millis() - tempo_ult_debouce4) > delay_debouce4){
            est_ini_por4 = 1; // fechada
            tempo_ult_debouce4 = millis();
        }
    }
    else{
        if (est_ini_por4 == 1 && analogRead(sens_porta1) < 4000){
            est_ini_por4 = 0; // aberta
            prim_press3 = 1;
        }
    }
    
    if(est_ini_por1 == 1 && prim_press2 == 1){ 
        prim_press4 = 1; 
        prim_press2 = 0;
        estado_luz = HIGH;  // primeira leitura de porta aberta -> estado_luz = HIGH
        tempo_alarme = tempo_atual;
        estado_verde = HIGH;
        estado_vermelho = HIGH;
    }
    if (est_ini_por1 == 1){
        if (tempo_atual >= tempo_alarme + delay_alarme && prim_press4 == 1){
            prim_press4 = 0;
            alarme_tocando = HIGH;
        }
    }
    
    if(est_ini_por1 == 0 && prim_press3 == 1){
        prim_press3 = 0;
        estado_luz = LOW;  // primeira leitura de porta fechada -> estado_luz = LOW
        estado_vermelho = LOW;
        estado_verde = HIGH;
        alarme_tocando = LOW;
    }

    if(analogRead(botao_AP) > 3000 && est_ini_bot == 0){  //detecção aperto botão alarme/luz
        if((millis() - tempo_ult_debouce3) > delay_debouce3){
            est_ini_bot = 1; //pressionado
            tempo_ult_debouce3 = millis();
        }
    }
    else if(analogRead(botao_AP) <= 3000 && est_ini_bot == 1){
        if(est_ini_bot == 1 && digitalRead(botao_AP) == LOW){
            est_ini_bot = 0; //não pressionado
            prim_press = 1;
        }
    }

    if(est_ini_bot == 1 && prim_press == 1){   //primeiro pressionamento botão
        prim_press = 0;
        estado_botao = HIGH;
    }
    else{
        estado_botao = LOW;
    }

    if(estado_botao == HIGH){    //controle luz interna -> alterna estado da luz
        if(alarme_tocando == HIGH){
            alarme_tocando = LOW;
        }
        else{
            if(estado_luz == LOW){
                estado_luz = HIGH;
            }
            else{
                estado_luz = LOW;
            }
        }
    }

    if(estado_luz == HIGH){
        digitalWrite(luz_interna, HIGH);
    }
    else{
        digitalWrite(luz_interna, LOW);
    }
    if(alarme_tocando == HIGH){
        digitalWrite(alarme, HIGH);
    }
    else{
        digitalWrite(alarme, LOW);
    }
    if (estado_verde == HIGH){
        digitalWrite(RGBverde, HIGH);
    }
    else{
        digitalWrite(RGBverde, LOW);
    }
    if (estado_vermelho == HIGH){
        digitalWrite(RGBvermelho, HIGH);
    }
    else{
        digitalWrite(RGBvermelho, LOW);
    }
    //Serial.println(digitalRead(botao_AP));
    Serial.println(analogRead(botao_AP));
}

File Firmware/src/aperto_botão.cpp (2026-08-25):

int botao = GPIO X;

long tempo_ult_debouce = 0;
long delay_debouce = 10;

int est_ini_bot = 0;

bool prim_press = true;

void setup(){
    pinMode(botao, OUTPUT);
}
void loop(){
    if(digitalRead(botao) == HIGH && est_ini_bot == 0){
        if((millis() - tempo_ult_debouce) > delay_debouce){
            est_ini_bot = 1; //pressionado
            tempo_ult_debouce = millis();
        }
    }
    else{
        if(est_ini_bot == 1 && digitalRead(botao) == LOW){
            est_ini_bot = 0;
            prim_press = true;
        }
    }
    if(est_ini_bot == 1 && prim_press == true){ //botão foi pressionado uma vez
        prim_press = false;
    }
}

/*LIGA DEIGA
int botao = 2;
int LED = 10;

long tempo_ult_debouce = 0;
long delay_debouce = 10;
unsigned long tempo_fporta1 = 0;

int est_ini_bot = 0;
int estado_botao = LOW;

int prim_press = 1;

void setup(){
  Serial.begin(9600);
  pinMode(botao, INPUT);
  pinMode(LED, OUTPUT);
  pinMode(4, OUTPUT);
  digitalWrite(4,HIGH);
}
void loop(){
  if(digitalRead(botao) == HIGH && est_ini_bot == 0){
    if((millis() - tempo_ult_debouce) > delay_debouce){
      est_ini_bot = 1; //pressionado
      digitalWrite(LED, HIGH);
      tempo_ult_debouce = millis();
        }
    }
  else{
    if(est_ini_bot == 1 && digitalRead(botao) == LOW){
      digitalWrite(LED, LOW);
      est_ini_bot = 0;
      prim_press = 1;
        }
    }
  if(est_ini_bot == 1 && prim_press == 1){   //condição do botão pressionado 
    prim_press = 0;
    if(estado_botao==LOW){   //se estiver em estado LOW
      estado_botao=HIGH;    //mudar para estado HIGH
            }   
    else if(estado_botao==HIGH){                    //condição botão não pressionado
      estado_botao=LOW;     //mudar de estado HIGH para estado LOW
            }
        }
    if(estado_botao==HIGH){
      digitalWrite(LED, HIGH);
    }
    else if(estado_botao==LOW){
      digitalWrite(LED, LOW);
    }
    
}

*/

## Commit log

2022-11-21 MecaVac primeiro commit
    [Main.SchDoc, MecaVac.PrjPcb]
2022-11-22 pcb progress
2022-11-28 Mudando o nome
    [Main.SchDoc]
2022-12-25 a baby
    [MecaVac.GBL, MecaVac.GBO, MecaVac.GBP, MecaVac.GBS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]
2022-12-28 update 27/12/2022- Gerber + Pick and Place
    [MecaVac.GBL, MecaVac.GBO, MecaVac.GBP, MecaVac.GBS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]
2023-11-25 Added Prototype New Version
    [MecaVac NEW.PrjPcb, MecaVac NEW.SchDoc]
